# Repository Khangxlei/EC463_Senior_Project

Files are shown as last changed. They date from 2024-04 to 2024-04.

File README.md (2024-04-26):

# EC464 Senior Project: 40Hz Light Therapy

This README includes a brief overview and an introduction to how to get started on our project. 

## Project Overview

### Introduction

This project aims to develop an LED panel capable of emitting a consistent 40Hz flickering light. The 40Hz frequency is particularly chosen based on research suggesting its potential benefits in neurotherapeutic applications, especially for enhancing cognitive functions and possibly impacting disorders like Alzheimer's disease.

### Objectives

The primary objective of this project is to design and construct a reliable, efficient LED panel system that can maintain precise flicker frequencies, especially targeting the 40Hz range. Key goals include:

 - Precision: Achieve exact control over flicker frequency to ensure consistent 40Hz output.
 - Safety: Ensure the panel operates safely under all conditions, including extensive usage scenarios.
 - User-Friendliness: Develop a control interface that allows users to easily adjust and set the brightness as needed.

### Current State

The project has reached a significant milestone with the development of two final product models:

 - **T0 Model:** This is the base model featuring a large LED panel that can simply turn on and off, designed for stationary use where size and portability are not constraints.
 - **T9 Model:** A compact, innovative model that can attach to any modern smartphone case using Velcro. The T9 not only offers portability but also includes adjustable flickering brightness settings, making it ideal for personal use in a variety of settings.

## Installation

Installation comes in two parts: the software and the hardware. Here are the steps to help you get a quick-start on our project:

1. First you should install the software part of the project. Please refer to the Installation section under the [README_software.md](README_software.md) file
2. Next, you can set up the hardware of the project. Please refer to the section named "_Setting up the product_" under the [README_hardware.md](README_hardware.md) file. If you need help acquiring the materials needed, under the same file there is a Bill of Materials (BOM) section where you can find all the materials you will need for the project.
3. After completing all these steps, you should be all set for installment!

## System Overview

For this product we have 2 different models catered towards different purposes. The base model, which is the T0, is our very first version for our client’s needs, which serves to be a simple LED panel supported by a stand. We then have the T9 model that is more streamlined and compact compared to the T0 model, and serves for a more user-friendly experience.

### T0

The phone would be attached onto the panel using an integrated phone holder, and at the back of the panel is where the power button resides. Simply, press it and the user will be able to use their phone without having to hold it, while being exposed to 40Hz light that is proven to help with Alzheimer’s Disease and dementia. The figure down below shows that we have the power supply being the wall outlet connected to the power module that will help power up the circuit. The panel stand will hold the LED panel, in which we have an Arduino Nano as the microcontroller connecting the hardware and software components that will act as the controller to transfer an ON/OFF signal into the LED panel. 

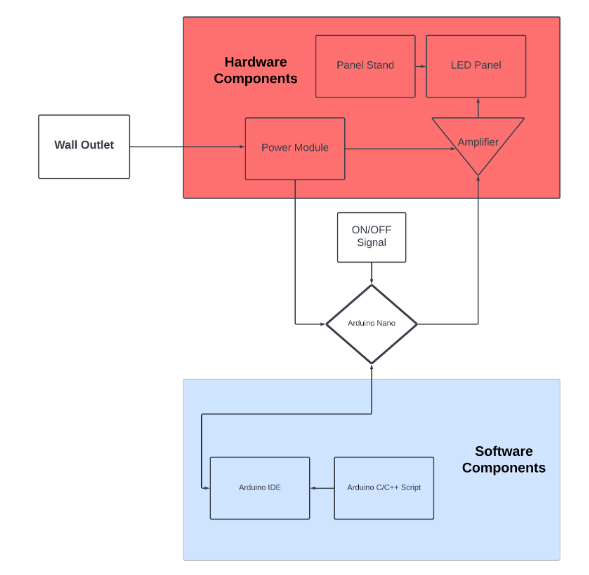
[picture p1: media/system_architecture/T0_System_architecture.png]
T0 System Architecture
 
  
[View PDF of T0 System Architecture](media/system_architecture/T0_System_architecture.pdf)

### T9

The figure down below is the overall system block diagram for the T9 model. It is a lot more streamlined and compact compared to the T9 model and is tailored more towards user’s convenience and needs. It has a phone cable that connects the phone into the microcontroller, which takes input of the brightness module and sends the corresponding signal to adjust the brightness of the LED accordingly. The software components for both models stay relatively the same as they are both compatible with Arduino code. 

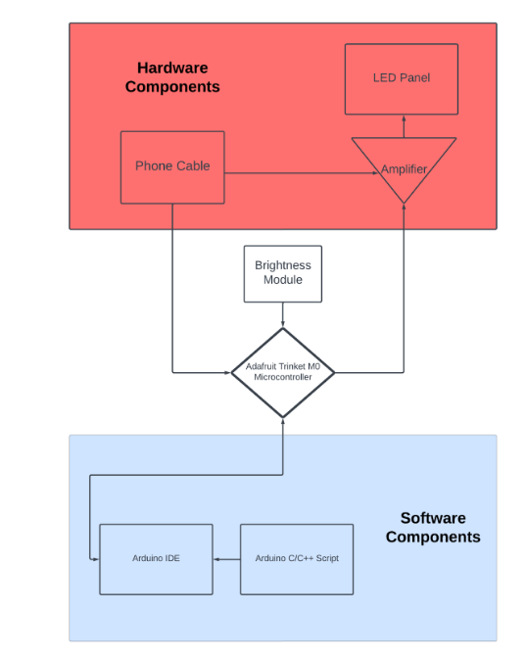
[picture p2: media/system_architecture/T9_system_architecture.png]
T9 System Architecture

  
[View PDF of T9 System Architecture](media/system_architecture/T9_system_architecture.pdf)

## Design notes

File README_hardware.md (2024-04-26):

# Hardware Schematics

## Circuit Diagram 

### T0
This is our circuit diagram for the T0 model. It uses pins 3, 4, and 5 as inputs and pins 5V and Ground as outputs. The circuit diagram illustrates an Arduino Nano wired with a button and a MOSFET towards an LED.
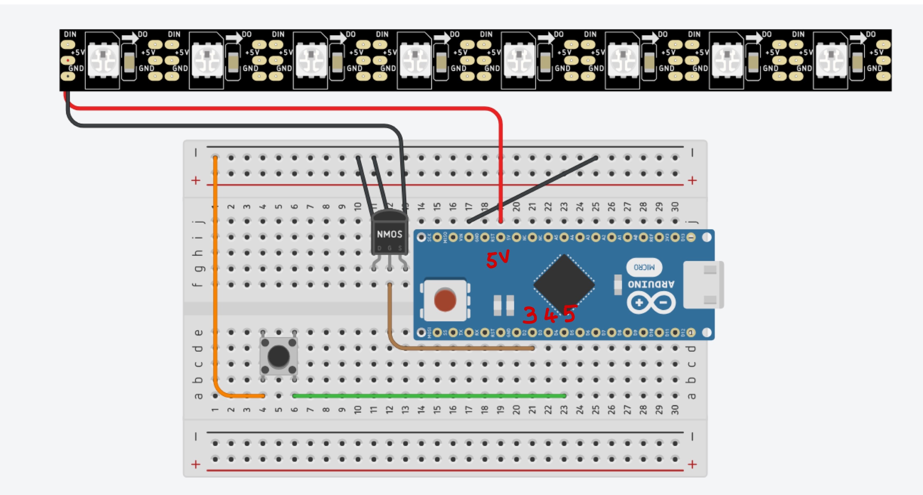
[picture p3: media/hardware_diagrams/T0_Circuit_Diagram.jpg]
Preview of T0 Circuit Diagram

[View PDF of T0 Circuit Diagram](media/hardware_diagrams/T0_Circuit_Diagram.pdf)

### T9
This is our circuit diagram for the T9 model. It uses pins 0, 3, and 4 as inputs and pins 3V and Ground as outputs. The circuit diagram illustrates an Arduino Nano wired with 2 buttons and a MOSFET towards an LED.

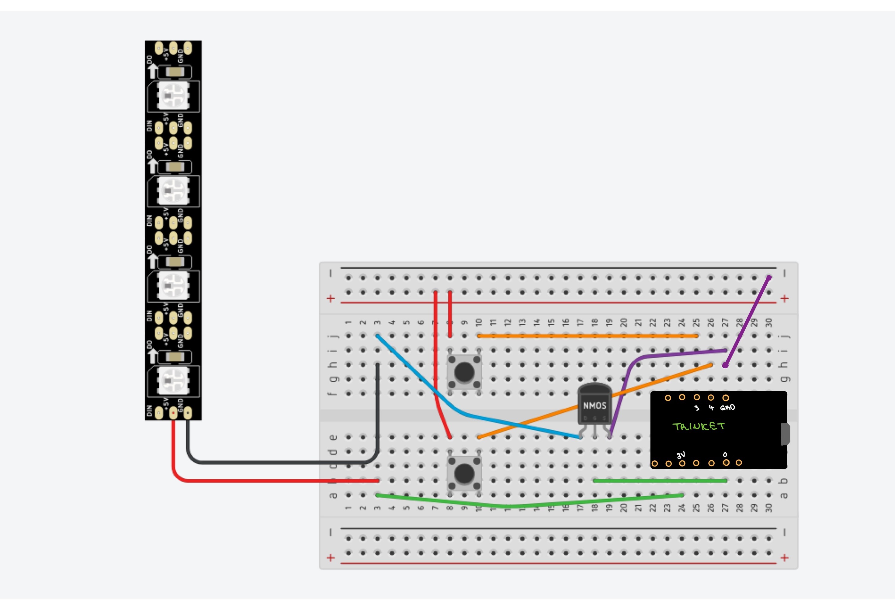
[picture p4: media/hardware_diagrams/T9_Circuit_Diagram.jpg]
Preview of T9 Circuit Diagram

[View PDF of T9 Circuit Digram](media/hardware_diagrams/T9_Circuit_Diagram.pdf)

## CAD Design

### T0 Housing

This is the CAD design for our T0 Housing. It consist of one button integrated along with an area for users to plug in the power cable to turn on the model. We have also uploaded the .stl file under the _hardware_diagrams/CAD_ folder and attached a PDF version of the CAD design down below.

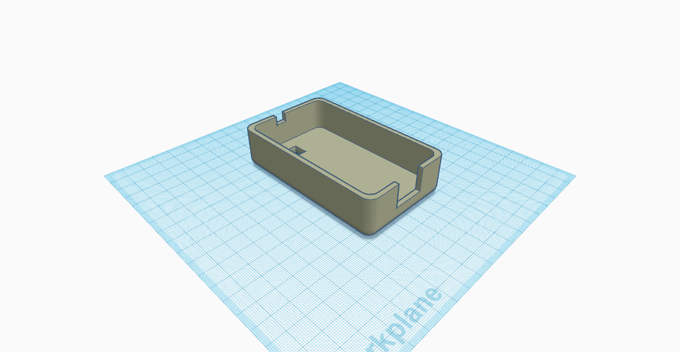
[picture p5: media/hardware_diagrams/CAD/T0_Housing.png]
T0 Housing
 [View PDF of T0 Housing](media/hardware_diagrams/CAD/T0_Housing.pdf)   

#### CAD File (.STL) 
Download the STL file for the T0 Model CAD design here: 
- [T0 STL CAD File)](media/hardware_diagrams/CAD/T0_Housing.stl)

### T0 Panel Stand
We used a pre-existing CAD design for a panel stand. This design allows 5 different angle configurations for the user to use the panel at whichever height they desire. We have also uploaded the .stl file under the _hardware_diagrams/CAD_ folder and attached a PDF version of the CAD design down below.

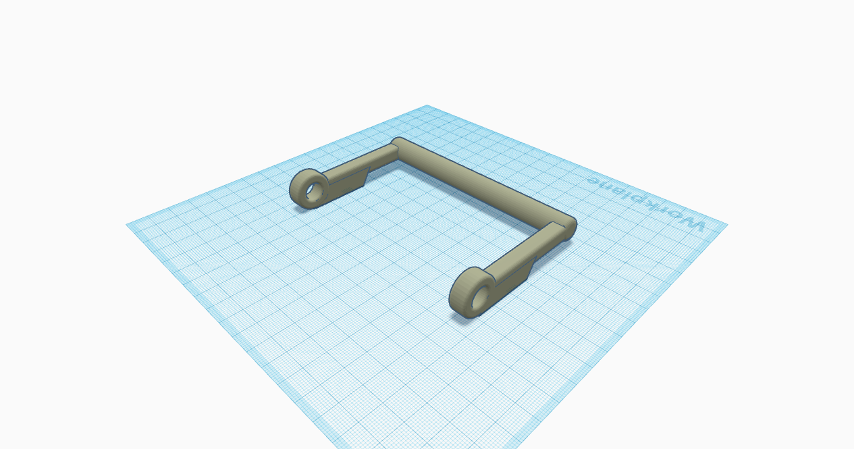
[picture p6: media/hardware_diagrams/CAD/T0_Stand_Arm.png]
T0 Stand Arm
 [View PDF of T0 Stand Arm](media/hardware_diagrams/CAD/T0_Stand_Arm.pdf)   
   
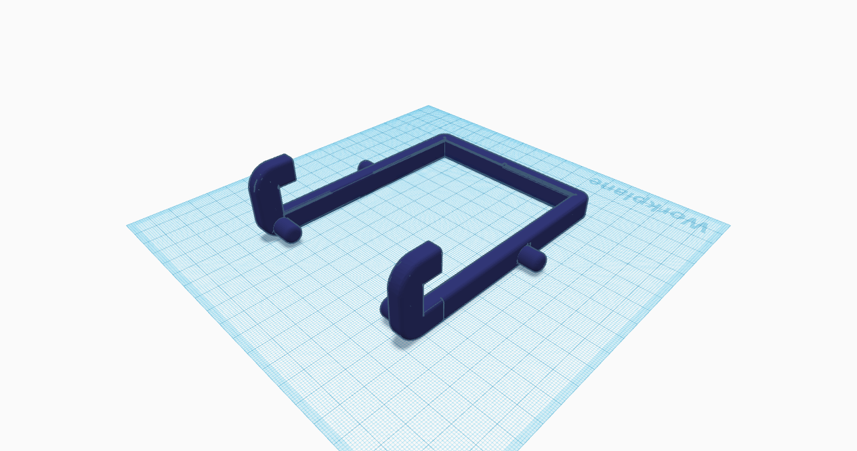
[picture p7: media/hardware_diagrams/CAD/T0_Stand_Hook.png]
T0 Stand Hook
 [View PDF of T0 Stand Hook](media/hardware_diagrams/CAD/T0_Stand_Hook.pdf)    
   
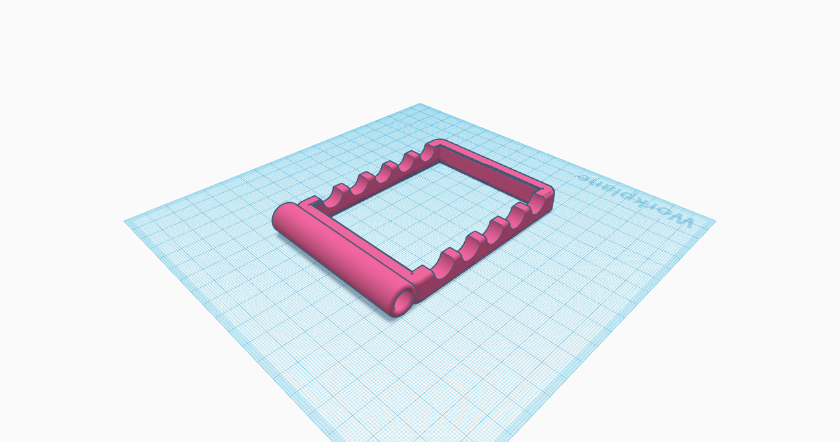
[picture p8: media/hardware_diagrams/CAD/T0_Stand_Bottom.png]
T0 Stand Bottom
 [View PDF of T0 Stand Bottom](media/hardware_diagrams/CAD/T0_Stand_Bottom.pdf)    

#### CAD File (.STL)
Download the STL file for the T0 Model CAD design here: _Emily should send the .stl files and replace that with this_
- [T0 Stand STL CAD File (1/3)](media/hardware_diagrams/CAD/T0_Stand_Arm.stl)
- [T0 Stand STL CAD File (2/3)](media/hardware_diagrams/CAD/T0_Stand_Bottom.stl)
- [T0 Stand STL CAD File (3/3)](media/hardware_diagrams/CAD/T0_Stand_Hook.stl)
  
### T9
This is the CAD design for our T9 Housing. It consist of 2 buttons integrated, along with a hollow bridge that allows the wires to run from the circuit board to the LED that is placed along the small panel above. It also has an open area to allow users to plug in their power cable. The .stl file is under the _hardware_diagrams/CAD_ folder and attached a PDF version of the CAD design down below.

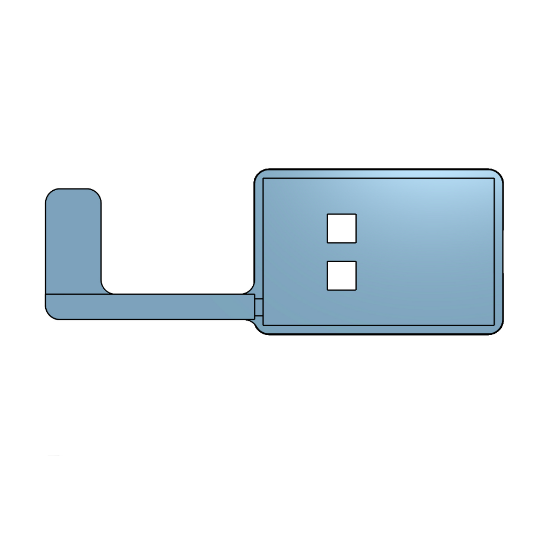
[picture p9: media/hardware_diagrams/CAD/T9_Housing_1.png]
T9 Housing (1/3)
 
   
[View PDF of T9 Housing 1](media/hardware_diagrams/CAD/T9_Housing_1.pdf)   
   
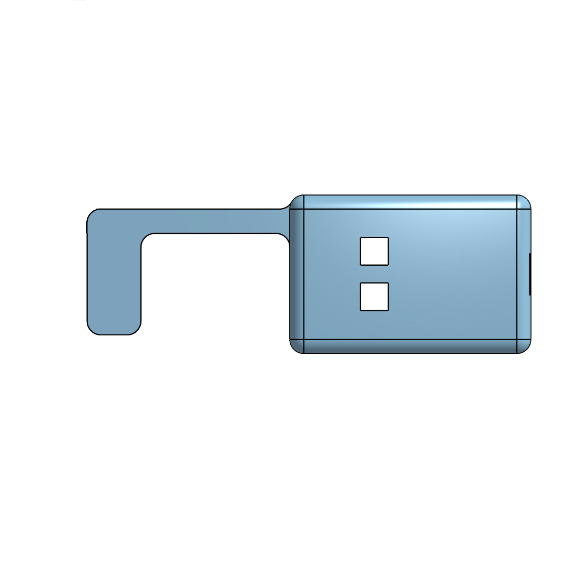
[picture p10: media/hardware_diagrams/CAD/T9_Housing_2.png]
T9 Housing (2/3)
 
   
[View PDF of T9 Housing 2](media/hardware_diagrams/CAD/T9_Housing_2.pdf)    
   
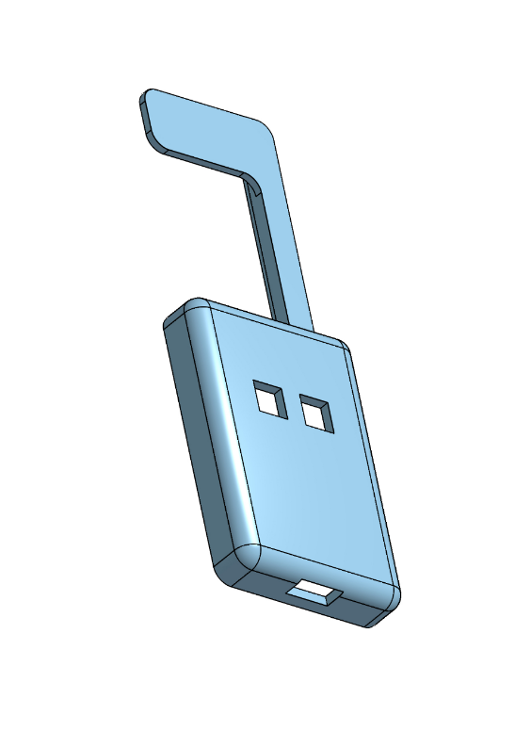
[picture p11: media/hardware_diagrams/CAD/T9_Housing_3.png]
T9 Housing (3/3)
 
   
[View PDF of T9 Housing 3](media/hardware_diagrams/CAD/T9_Housing_3.pdf)    

#### CAD File (.STL)
Download the STL file for the T9 Model CAD design here:
- [T9 STL CAD File (1/3)](media/hardware_diagrams/CAD/T9_Trinket_housing_cover.stl)
- [T9 STL CAD File (2/3)](media/hardware_diagrams/CAD/T9_Trinket_housing.stl)
- [T9 STL CAD File (3/3)](media/hardware_diagrams/CAD/T9_prototyping_board_housing.stl)

# Bill of Materials (BOM)
The following table includes a detailed list of all the materials used in the project, along with vendor information for each component:

| Item No. | Component                    | Quantity | Vendor Name        | Part Number | Price  |
|----------|------------------------------|----------|--------------------|-------------|--------|
| 1        | Adafruit Trinket M0 Trinket  | 1        | Adafruit           | 3500        | $8.95  |
| 2        | Arduino Nano + Cable         | 1        | Arduino            | A000005     | $24.90 | 
| 3        | Prototype Circuit Board      | 2        | Amazon             | B081MSKJJX  | $7.99  |
| 4        | LED Strip                    | 2        | Amazon             | B0C9919Z7Q  | $14.99 |
| 5        | LED Panel                    | 1        | Amazon             | B09VTCG1ZR  | $14.99 |
| 6        | Wires                        | 10-15    | Boston University  | N/A         | N/A    |
| 7        | Button                       | 3        | Boston University  | N/A         | N/A    |
| 8        | MOSFET                       | 2        | Boston University  | N/A         | N/A    |
| 9        | Velcro                       | 1        | Amazon             | 085-03-0026 | $9.29  |
| 8        | Micro-USB to USB-C Cable     | 1        | Amazon             | B094RDLNDB  | $9.99  |

## Vendor Information
Below is additional information about the vendors from whom components were purchased:

- **Adafruit Industries**
  - **Website:** [Adafruit.com](https://www.adafruit.com)
  - **Contact:** support@adafruit.com
  - **Phone:** (646) 248-7822

- **Arduino**
  - **Website:** [Arduino.cc](http://arduino.cc)
  - **Contact:** support@arduino.cc
  - **Phone:** N/A

- **Amazon**
  - **Website:** [Amazon.com](https://www.amazon.com/)
  - **Contact:** [Amazon Contact Page](https://www.amazon.com/gp/css/contact-us-access/ref=cu_surl_text_trace)
  - **Phone:** 1-888-280-4331

# Power Requirements

This section outlines the power specifications required to operate the 40Hz LED Panel effectively.

## T0 
### Voltage Requirements
- **Operating Voltage:** 5V
- **Minimum Voltage:** 0V
- **Maximum Voltage:** 5V

### Current Requirements
- **Operating Current:** 2 A
- **Peak Current:** 2.4 A (during operation)
- **Standby Current:** 10mA ~ 100mA (when idle)

### Power Consumption
- **Typical Power Consumption:** 10 Watts
- **Maximum Power Consumption:** 12 Watts (under full load)

## T9
### Voltage Requirements
- **Operating Voltage:** 3V
- **Minimum Voltage:** 0V
- **Maximum Voltage:** 3V

### Current Requirements
- **Operating Current:** 2 A
- **Peak Current:** 2.4 A (during operation)
- **Standby Current:** 10mA ~ 100mA (when idle)

### Power Consumption
- **Typical Power Consumption:** 6 Watts
- **Maximum Power Consumption:** 7.2 Watts (under full load)

### Additional Notes
- Make sure to use a power supply that matches or exceeds the required specifications.
- Avoid exposing the device to voltages above the maximum rating to prevent damage.
- For optimal performance, ensure stable current delivery especially during peak usage.

# System Pictures

This section provides a clear view of the system inside the enclosure. 

## T0 (inside enclosure)

These are pictures of the system circuit for the T0 model. This is what is inside the enclosure, before we placed a housing over it. The pictures displays the circuit board with the components that we used for the T0 model.

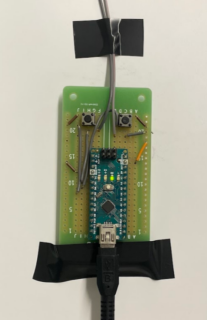
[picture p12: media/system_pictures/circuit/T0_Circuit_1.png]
System Circuit (1)

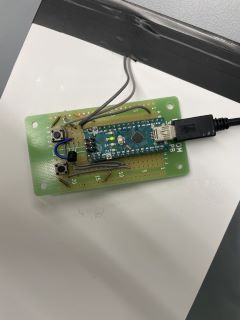
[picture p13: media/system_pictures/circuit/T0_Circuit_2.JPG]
System Circuit (2)


## T9 (inside enclosure)

The picture below shows the system for the T9 model. The two yellow wires are the power and ground wires connecting towards the LED. 

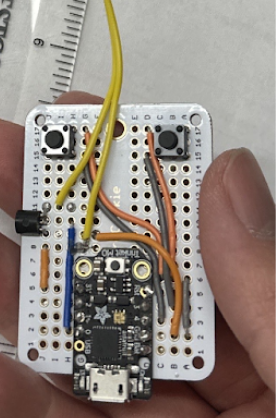
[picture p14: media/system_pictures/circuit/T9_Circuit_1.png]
System Circuit (1)


## T0 (with enclosure)

These are pictures of the system circuit for the T0 model. This is what is inside the enclosure, before we placed a housing over it. The pictures displays the circuit board with the components that we used for the T0 model.

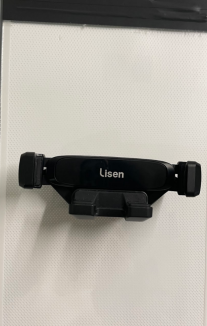
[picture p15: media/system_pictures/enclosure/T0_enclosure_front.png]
T0 Complete Circuit Front

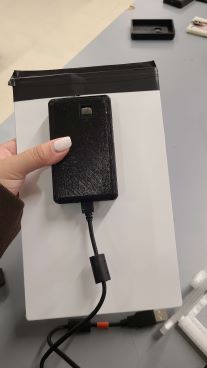
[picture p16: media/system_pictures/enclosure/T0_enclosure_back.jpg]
T0 Complete Circuit Back


## T9 (with enclosure)

The video below is a full demonstration of the T9 model. It is small and compact and there are buttons in the back that are used to adjust the brightness intensity of the LED. 

T9 Video with Enclosure

# Setting up the product

This section will document how to set up the hardware part of our project. For instructions on how to install the software system, please refer to the README_software.md. 

## T0

Place the phone onto the phone holder compartment at the front of the panel (illustrated below). 

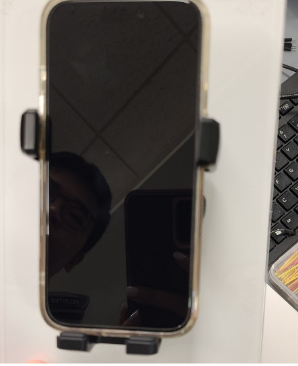
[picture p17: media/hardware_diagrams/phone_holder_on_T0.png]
Phone on Holder of T0


Now set up a circuit with the following schematic, same as the one that was shown in the circuit schematics section. Make sure to use the correct pins on the Arduino Nano!

Preview of T0 Circuit Diagram

From then, simply plug in the power cable for the Arduino Nano, click on the button and you should have a functioning 40 Hz flickering LED panel!

## T9

Setting up the T9 model is a lot simpler. Simply create the following circuit using the schematic below. From there, power the microcontroller using a micro-USB to USB-C cable and adjust the brightness using the two buttons. 

Preview of T9 Circuit Diagram

# Pictures of Final Product

## T0

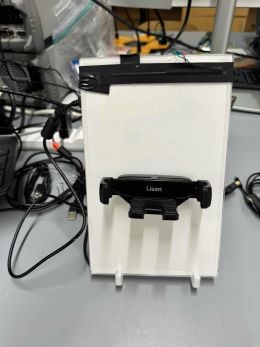
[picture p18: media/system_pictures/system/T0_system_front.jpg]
Picture of T0 System (Front)

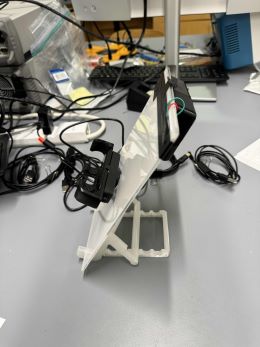
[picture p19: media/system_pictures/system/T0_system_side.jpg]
Picture of T0 System (Side)

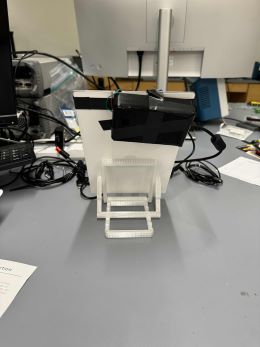
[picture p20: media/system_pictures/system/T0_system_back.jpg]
Picture of T0 System (Back)

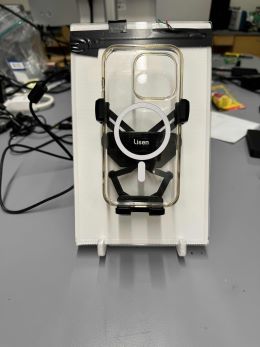
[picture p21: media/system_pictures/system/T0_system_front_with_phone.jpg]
Picture of T0 System (Front with Phone)


## T9

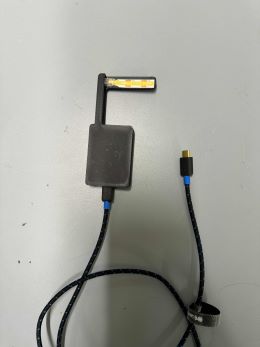
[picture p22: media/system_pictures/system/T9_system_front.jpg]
Picture of T9 System (Front)

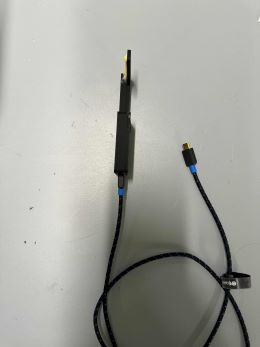
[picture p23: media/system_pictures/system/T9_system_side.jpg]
Picture of T9 System (Side)

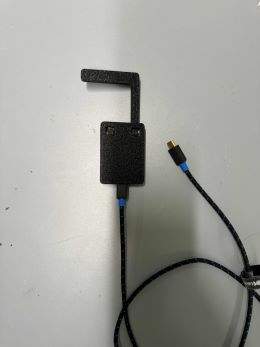
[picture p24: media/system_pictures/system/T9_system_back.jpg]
Picture of T9 System (Back)


# Notes
## Datasheets
 - [Datasheet for Trinket M0](https://cdn-learn.adafruit.com/downloads/pdf/adafruit-trinket-m0-circuitpython-arduino.pdf)
 - [Datasheet for Arduino Nano](https://docs.arduino.cc/resources/datasheets/A000005-datasheet.pdf)

## Web resources
 - [Arduino Nano Documentation](https://docs.arduino.cc/hardware/nano/)
 - [Operating LED Documentation](https://img.kwcdn.com/product-file-public/1fa3201b30/e1cf93ef936620d4e02b9221dc2b4623.pdf?_x_sessn_id=po0ericp0z&refer_page_name=goods&refer_page_id=10032_1714006419912_5y583ihzke&refer_page_sn=10032)
 - [Adafruit Trinket M0 Documentation](https://www.play-zone.ch/en/fileuploader/download/download/?d=1&file=custom%2Fupload%2FFile-1507818705.pdf)

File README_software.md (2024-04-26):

# Software

Since our project is mainly hardware, there is not much documentation needed for the software aspect of this project.

## Files

There are 2 files we have developed on Arduino IDE of file type: .ino, each of which are in charge of controlling our two microcontrollers: Arduino Nano and Adafruit Trinket M0. They .ino files are named respectively to their own microcontroller, Arduino_Nano.ino & Trinket_M0.ino. 

### Arduino_Nano.ino

This file is in charge of programming logic for our T0 model, which utilizes the Arduino Nano as its microcontroller. The Arduino program takes in a singular input pin, which is the button on pin 4, and it takes in an output pin which goes towards the LED at pin 3. Programming logic is that it toggles the brightness on and off every 12.5ms, which is half of 25ms because 25ms = 1/f = 1/40Hz. The code also incorporates a debouncer to recognize when the user clicks a button, it turns the brightness off immediately. The delay would not be interfering with the 40Hz, as it only has a delay at the start or end of the blinking cycle, so during its blinking there should not be interference.

### Trinket_M0.ino

This file is in charge of programming logic for our T9 model, which utilizes the Adafruit Trinket M0 as its microcontroller. The program this time takes in 2 input pins, being pin 3 and 4 for increase and decrease brightness buttons. It follows a similar logic as Arduino_Nano.ino, the only difference is that this time, it has a brightness variable that continuously changes every time one of the button pins gets pushed, in which it sends a signal to the program and we set the brightness variable accordingly to the button (0 being the minimum and 255 being the maximum). The analogWrite then displays the LED at whichever brightness the variable is on, and therefore we can adjust the brightness for our T9 model.

## Installation

### Arduino_Nano.ino

Installation for the Arduino Nano is simple, since the Nano is already a default board within Arduino IDE. Here are the steps:
 - First ensure you have the Arduino IDE software installed. You can download it here: [Install Arduino IDE](https://www.arduino.cc/en/software)
 - Download the _Arduino_Nano.ino_ file onto your desktop.
 - Open it via Arduino IDE.
 - At the top, click on the Dropdown where it says "_Select Board_", then click on "_Select other board and port_". A pop-up should then open.

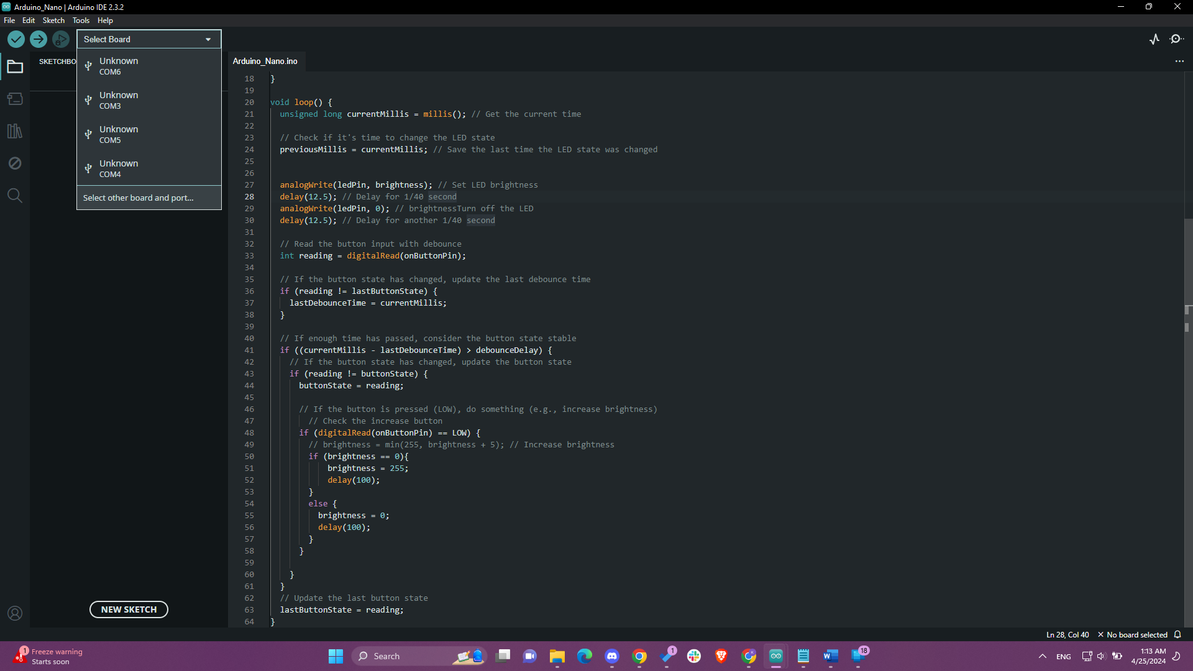
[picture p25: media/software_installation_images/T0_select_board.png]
Select board
   
   
 - On the pop-up, type in Nano and select "_Arduino Nano_", as well as the COM Port that you have the PC connected to with the Nano.

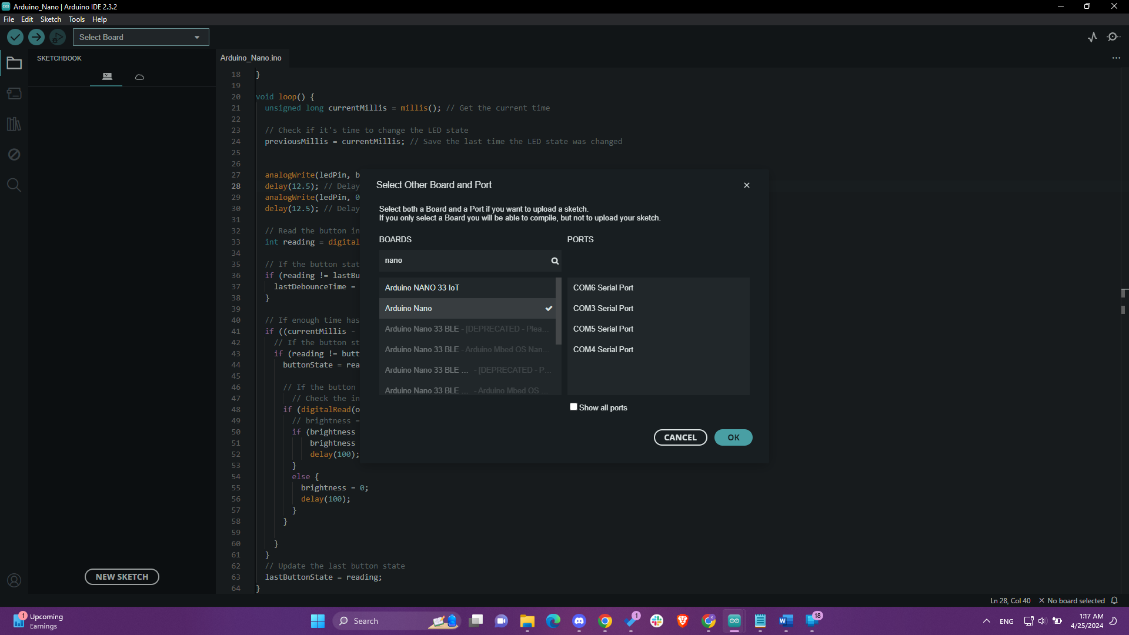
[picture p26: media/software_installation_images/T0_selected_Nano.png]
Selected board
   
   
 - Click OK.
 - Now simply click Upload (top left button with the arrow icon pointing to the right) and your code should now be embedded into the Arduino Nano!

### Trinket_M0.ino

 - First ensure you have the Arduino IDE software installed. You can download it here: [Install Arduino IDE](https://www.arduino.cc/en/software)
 - Download the _Trinket_M0_.ino_ file onto your desktop.
 - Open it via Arduino IDE.
 - At the top right, click Files > Preferences, or you can do it on your keyboard: Ctrl+Comma. At the bottom of the Preferences tab, there is a user input area for "_Additional boards manager URLs_". Paste in this link: <https://adafruit.github.io/arduino-board-index/package_adafruit_index.json>. If there are other links present, separate them with comma.

 Additional boards manager URLS

 - Next, open Boards Manager by clicking on Tools > Board > Boards Manager.
   
 Boards Manager

 - Search Arduino SAMD, and install the latest version of “Arduino SAMD Boards (32-bits ARM Cortex-M0+) by Arduino.

 SAMD Arduino

 - Next, search Adafruit SAMD, and install the latest version of Adafruit SAMD Boards by Adafruit. By now, you should be able to find the Trinket M0 in your list of boards. 

SAMD Adafruit

 - Close Boards Manager.
 
 - At the top, click on the Dropdown where it says "_Select Board_", then click on "_Select other board and port_". A pop-up should then open.

   Select board
   
 - On the pop-up, type in Trinket M0 and select "_Adafruit Trinket M0 (SAMD21)_", as well as the COM Port that you have the PC connected to with the Nano.

   Selected board
   
 - Click OK.
 - Now simply click Upload (top left button with the arrow icon pointing to the right) and your code should now be embedded into the Trinket!

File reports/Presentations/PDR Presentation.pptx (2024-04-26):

## Team 9 - Alzheimer’s Therapy

Bailey Brake, Ruohui Huang, Emily Lampat, Khang Le,
Yuri Zhang

## Introduction and Problem Statement

- Light Therapy
- AlzLife
- Light Attachment
Alzheimer’s and Dementia affect millions of americans each year. There is no cure, however, management of the cognitive decline seen in patients diagnosed with dementia plays a vital role in maintaining their quality of life.

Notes: Alzheimer’s and Dementia affect millions of americans each year. There is no cure, however, management of the cognitive decline seen in patients diagnosed with dementia plays a vital role in maintaining their quality of life. Though there is no known cure, researchers continue to look into maintaining cognition of patients and managing symptoms. AlzLife has developed an application that flashes the users screen while they play cognitive games.

## Requirements and Deliverables

- Flash at 40Hz
- Light intensity is visible to user
  - Adjustable light intensity
- Attach to smartphone
- Intuitive for user
- Subtle & ergonomic electronics housing
- Smartphone powered

## System Block Diagram


## Hardware


Circuitry
- Initial prototyping: Arduino Nano board
- Upcoming prototype: Adafruit Trinket board
- LED strip
- Brightness control buttons
Housing
- Current design: focus on compactness, then implement ergonomics



## Software

Arduino Software (IDE)
Arduino programming language (based on C/C++)
- Adjust LED brightness with two buttons.
- Pins: LED (3), Increase Button (4), Decrease Button (5).
- Blink Rate: 12.5ms intervals (40Hz).
- Code Mechanics: Uses PWM for brightness, analogWrite for LED control.
- Interaction: Press to increase/decrease brightness by 5, range 0-255.

## Testing procedure & results

1. Ensure Arduino is connected to a computer that has access to the code (https://github.com/rhhuang01/EC463Code/blob/main/Arduino) that generates PWM.
2. Compile and upload the script via the Arduino IDE.
3. Observe the oscilloscope and verify that the LED flickers within our desired time period.
4. Press the buttons to verify brightness is getting higher and lower corresponding to its own designated button, while maintaining the correct flicker frequency.


Circuit Setup

## Testing procedure & results (Cont.)


## Schedule


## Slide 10

Comments/Questions

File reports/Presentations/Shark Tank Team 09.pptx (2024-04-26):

## OptiSync Therapy

Synchronizing Light, Improving Your Life
An AlzLife Technology

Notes: BRAINSTORM:
AlzLife Light Frame

## Value Proposition


- For participants in Alzheimer’s clinical study, seeking to improve their cognition and sleep
- Our solution is a light frame to provide 40Hz therapy to attach to any phone
- Current 40Hz light therapy means require time set aside for the therapy: ours does not
Our product will meaningfully improve the therapy experience for patients of Alzheimer’s and dementia

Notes: Note that sometimes you need more than one value proposition. For example if the beneficiary does not pay you, then you need one value proposition for your beneficiary and one for your paying customer.

## Possible implementation: a visualization


## Minimum Viable Product


We need a light that flashes at 40 Hz at a consistent and comfortable intensity
It must attach to any phone case

## Technology Solution


Point 1: Advanced LED technology delivering consistent 40Hz frequency, maximizing therapeutic effects.
Point 2: Energy-efficient design ensuring extended use with minimal power consumption
Future step: Smart integration with an app allowing for tracking, reminders, and real-time feedback on therapy progress.

## Thank you!






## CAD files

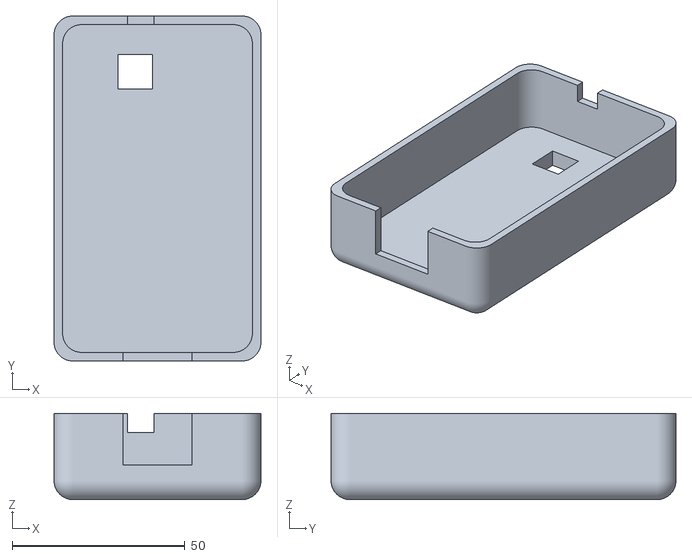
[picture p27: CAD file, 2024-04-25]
media/hardware_diagrams/CAD/T0_Housing.stl
60.0 x 100.0 x 25.0

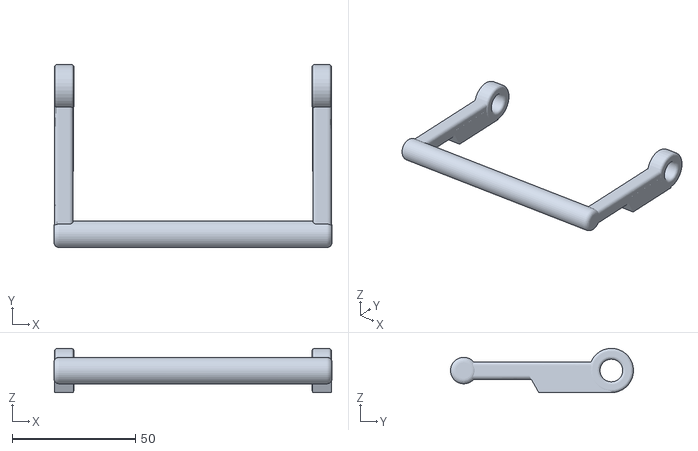
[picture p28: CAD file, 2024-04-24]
media/hardware_diagrams/CAD/T0_Stand_Arm.stl
113.0 x 74.4 x 18.0

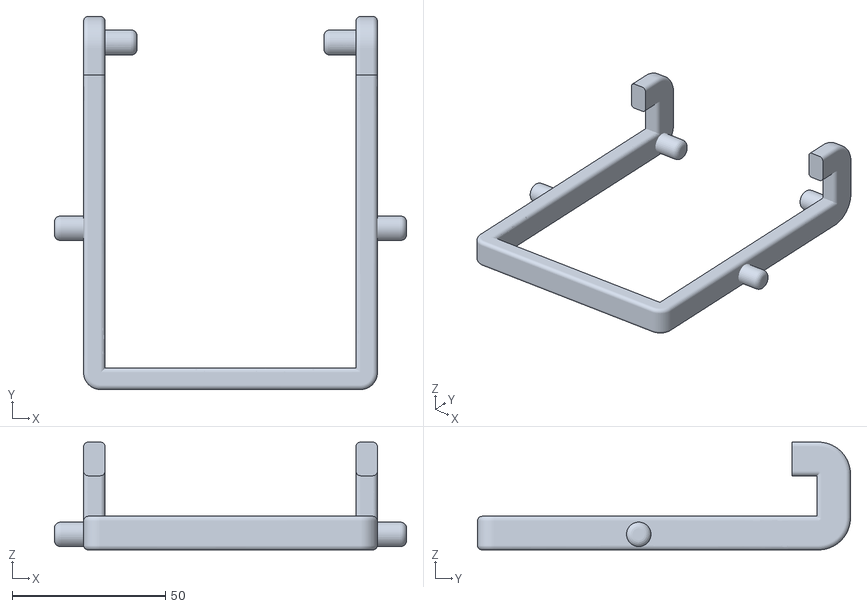
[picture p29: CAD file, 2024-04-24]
media/hardware_diagrams/CAD/T0_Stand_Hook.stl
115.2 x 121.9 x 35.2

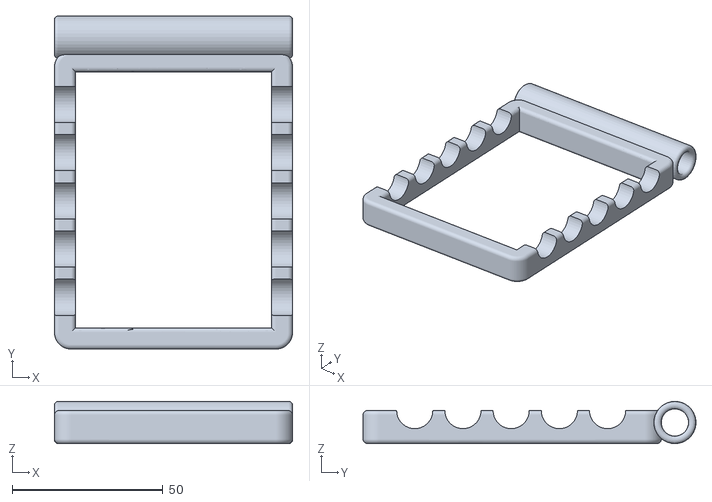
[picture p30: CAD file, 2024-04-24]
media/hardware_diagrams/CAD/T0_Stand_Bottom.stl
79.0 x 110.5 x 14.0

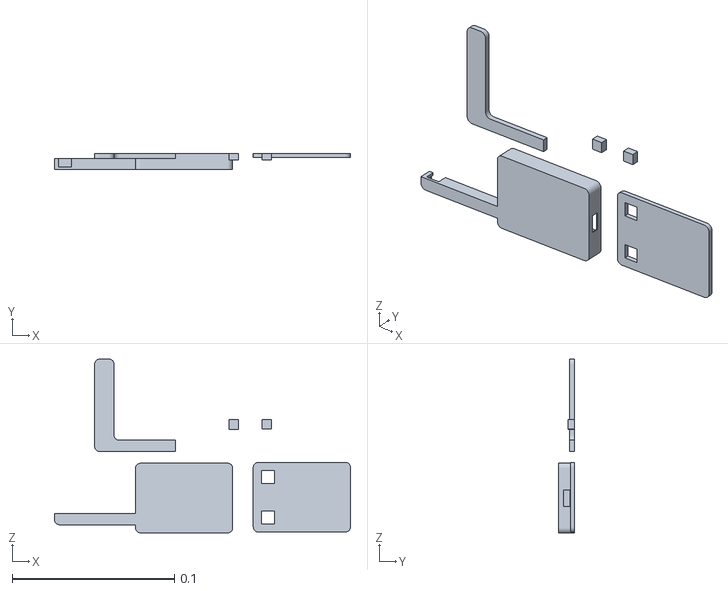
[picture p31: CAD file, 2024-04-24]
media/hardware_diagrams/CAD/T9_Housing_1.stl
0.183 x 0.01 x 0.107

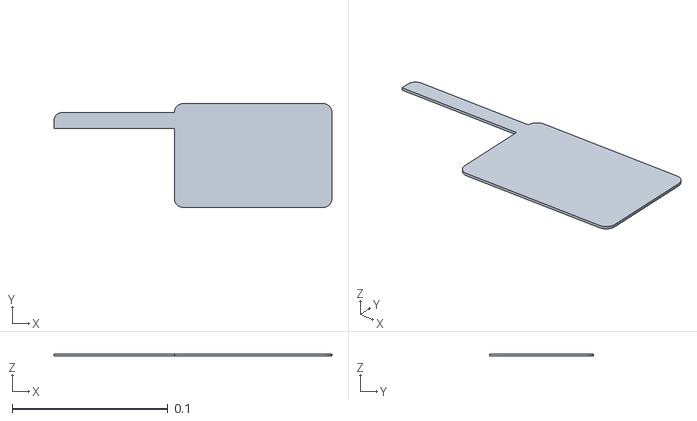
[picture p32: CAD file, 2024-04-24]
media/hardware_diagrams/CAD/T9_Housing_2.stl
0.178 x 0.0667 x 0.00146

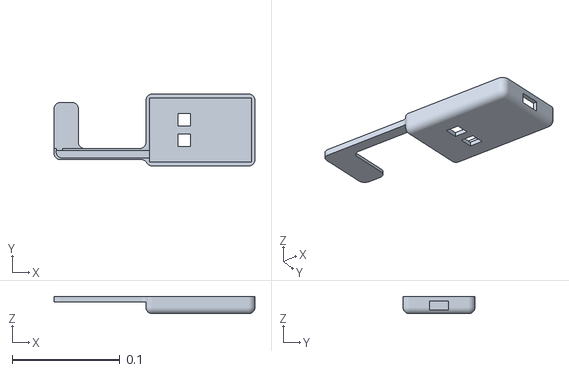
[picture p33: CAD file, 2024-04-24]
media/hardware_diagrams/CAD/T9_Housing_3.stl
0.186 x 0.0667 x 0.0161

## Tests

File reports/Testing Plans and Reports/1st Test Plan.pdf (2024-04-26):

# Boston University

# Electrical & Computer Engineering

## EC464 Senior Design Project

# Second Prototype Testing Plan

# OptiSync

by

Team 9

OptiSync

Team Members

Bailey Brake bbrake01@bu.edu

Ruohui Huang rhhuang@bu.edu

Emily Lampat lampat26@bu.edu

Khang Le khang@bu.edu

Yuri Zhang zyuri@bu.edu

1

### 1.0 Required Materials

Hardware:
- LED light
- Arduino Nano microcontroller
- Adafruit Trinket M0 microcontroller
- Circuitry Board
- Wires
- Buttons
Software:
- Arduino IDE
- Arduino script to generate 40Hz light frequency.
- Take buttons as input to write into LED output, acting as power source.

### 2.0 Set Up

Have the prototype where the circuitry board will be placed and stuck on the back of the LED panel. The wires will then connect from the Arduino Nano microcontroller into the LED that is placed at the front of our panel, We will also place a phone holder at the front that is glued onto it. Next, we will upload our code embedded into the Nano, plug it into a wall outlet and we are done with the setup.

### 3.0 Pre-Testing Setup Procedure

Pre-testing setup procedure is fairly simple. Please refer to the figures below to ensure that the setup is correct. All that is needed to do is connect the microcontroller into a wall plug and upload the

2

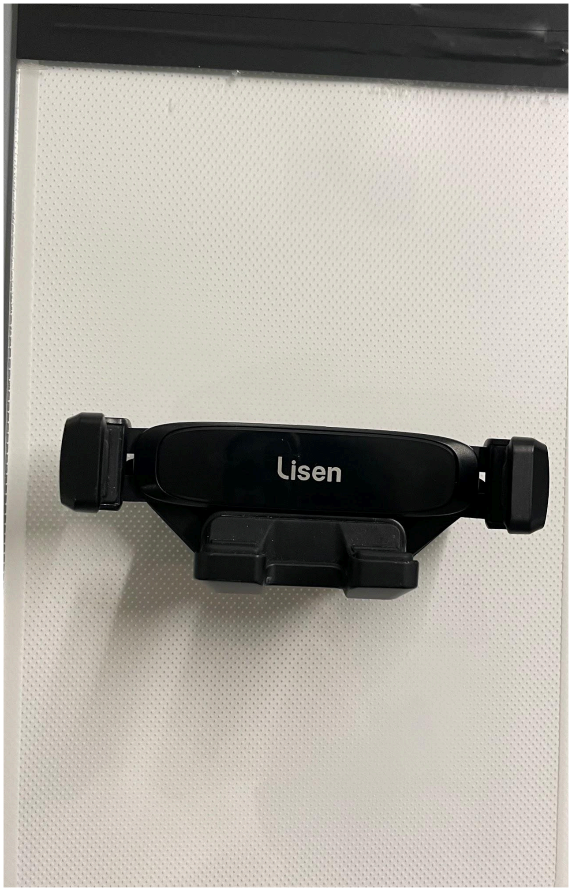
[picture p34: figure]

Figure 1. Front of LED Panel T0 Model

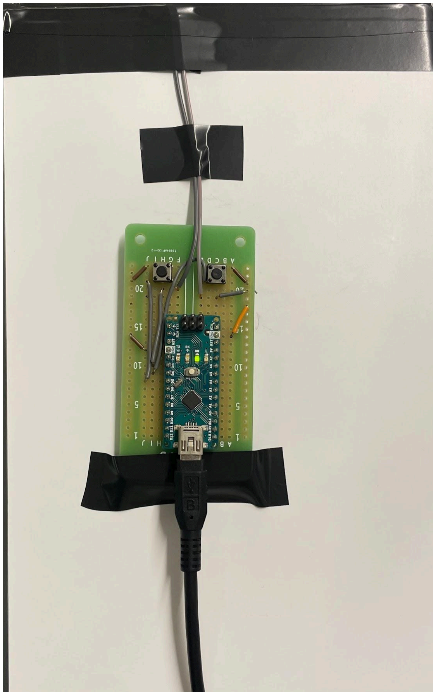
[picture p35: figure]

Figure 2. Back of LED Panel T0 Model

3

### 4.0 Testing Procedure

For the T0 model:
1. Ensure Arduino is connected to a wall outlet power source.
2. Verify that the LED status on the Arduino is lit up.
3. Press the button multiple times to verify the LED is receiving an ON/OFF signal.
4. Ensure that the phone holder is able to support the phone by placing the phone onto the holder attached to the panel.

### 5.0 Measurable Criteria

The criteria for having a successful running prototype are as follows
I. The circuit board should be intact with the LED panel.
II. | The LED should be at the front of the panel connected to the circuit board.
III. | Upon plugging in the microcontroller and pressing down the button, the LED should start
| flashing.
IV. | When toggling with the button, the LED should turn on and off within <1 second.

### 6.0 Hardware Pinout

T0 model:

Pin Number | Usage/Description
3 | White LED Output
4 | LED ON/OFF Button Input

4

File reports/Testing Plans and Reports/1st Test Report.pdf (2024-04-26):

# Memo

To: Professor Pisano
From: Yuri Zhang, Bailey Brake, Ruohui Huang, Emily Lampat, Khang Le Team: 9
Date: 11/19/2023
Subject: 1st Prototype Test Report

## 1.0 Test Setup

### 1.1 Bill of Materials:

| Hardware: ● LED Light: Selected for its efficiency and brightness, which are crucial for our application. ● Arduino Trinket Microcontroller: Chosen for its compact size and lack of unnecessary functions, making it ideal for our streamlined prototype. ● Oscilloscope: Essential for accurately measuring the LED's flicker frequency and ensuring our product meets the required specifications. ● Probes/Wires: For connecting and testing the circuit. ● Resistors: Calculated to match the LED's specifications, ensuring optimal current flow without risking damage. ● Laptop Computer: Used for programming the Arduino and monitoring the test. ● Tactile Push Buttons: For manual control over the LED's brightness levels. Software: ● Arduino IDE ○ Arduino script to generate 40Hz light frequency. ○ Take buttons as input to write into LED output, adjusting its brightness.

### 1.2 Setup Procedure:

| Our setup has been carefully designed to replicate a natural application environment.
| The Arduino Trinket is the central control unit connected to the laptop via a USB connection. This setup is essential for programming the microcontroller and allows real-time monitoring and adjustments during testing. An oscilloscope is used to continuously monitor the electrical characteristics of the LEDs, including flicker frequency and brightness levels. Two probes

1

from an oscilloscope were connected to the LED to measure the output frequency, given the difficulty of observing the 40Hz flicker rate with the naked eye.
The setup process involves careful calibration of the device. The LEDs are connected to the Arduino Trinket through a series of resistors and wires, ensuring that the current flowing through the LEDs is within safe limits. Tactile buttons are integrated into the circuitry to adjust the brightness of the LEDs manually. This setup aspect is essential because it simulates the end user's interaction with the product.

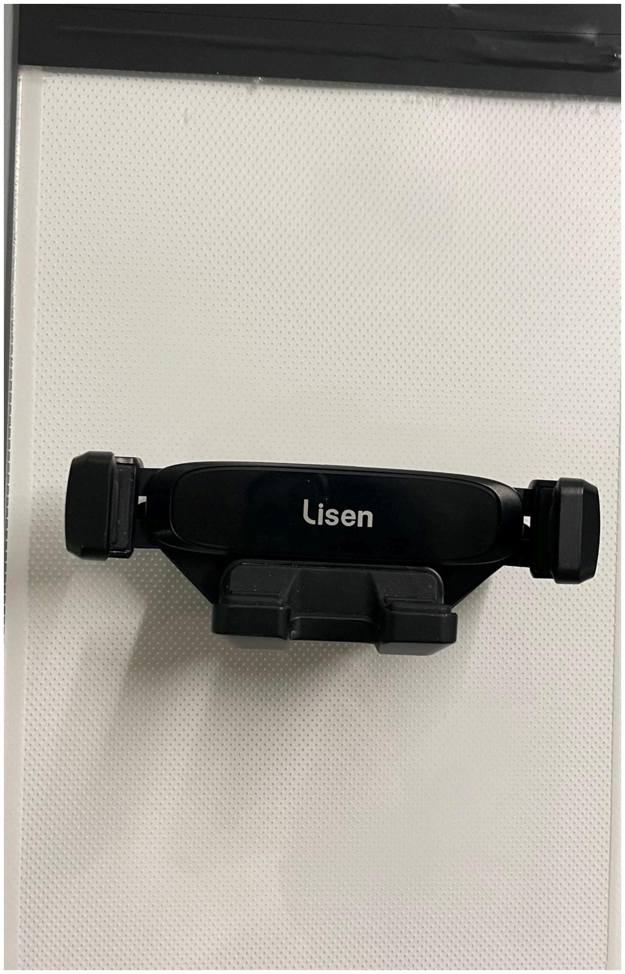
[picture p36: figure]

### Figure 1. Front of LED Panel T0 Model

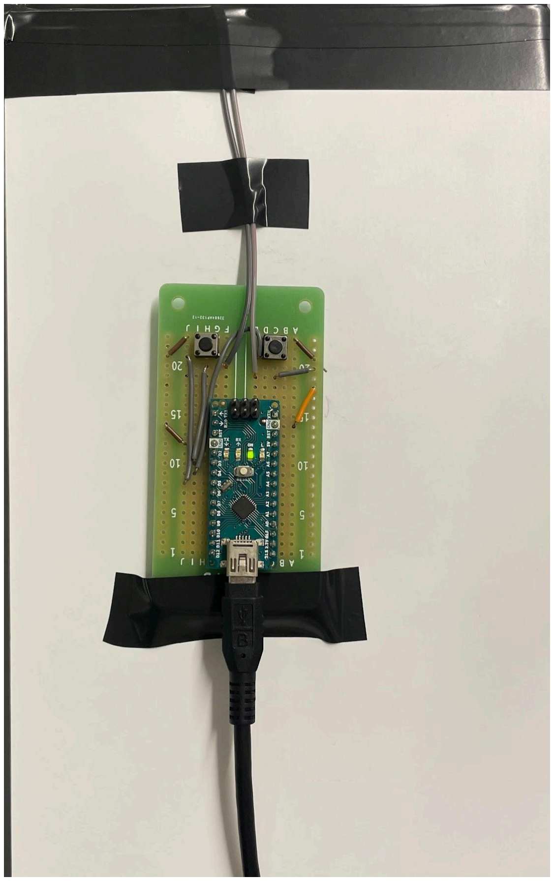
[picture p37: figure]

### Figure 2. Back of LED Panel T0 Model

2

### Figure 1: Illustration of Circuit Setup

## 2.0 Results and Measurements

### 2.1 Flicker Frequency Measurement:

In order to measure the flicker frequency, we set a time interval of 25ms on the oscilloscope, which is the desired time period of a flicker, considering we want 40Hz and t = 1/f = 1/40Hz = 0.025s. The LED's on-off cycle was observed to be consistent within this timeframe, with a deviation of less than 0.5ms, indicating high precision in frequency control.

### 2.2 Brightness Adjustment Measurement:

As for the brightness adjustments, we had two buttons separately increasing/decreasing the brightness. During our testing, as we pressed and held each button, the brightness gradually increased/accordingly reduced to the controller. Once it reached a maximum of brightness/dimness, it stayed there. We could turn it back on by pressing and holding the button. The brightness control was tested over a range of 0 to 255 in 10 increments. Each button press resulted in a smooth transition between brightness levels, with the oscilloscope showing a corresponding change in voltage across the LED. The maximum and minimum brightness levels were consistent across multiple tests, demonstrating the reliability of our control mechanism.

## 3.0 Conclusion and In-Depth Analysis

### 3.1 Conclusion:

The prototype test successfully demonstrated the core functionalities of our design. The Arduino script effectively maintained a 40Hz flicker frequency, which is crucial for our application's requirements. The manual brightness adjustments were responsive and precise, indicating a well-designed user interface.

### 3.2 Future Directions:

Our next steps involve transitioning to the Trinket M0 microcontroller for a more compact and efficient design. We will also integrate LED strips per our client's request and proceed with soldering to ensure robust and reliable connections. Further, we plan to conduct extensive user testing to refine the interface and ergonomics of our product.

### 3.3 Reflective Analysis:

The test setup and results aligned with our initial test plan, validating our equipment choices and design approach. The precision in flicker frequency control and the effective brightness adjustment mechanism were crucial achievements. In subsequent iterations, we will continue refining our design, enhancing circuit efficiency and user experience.

3

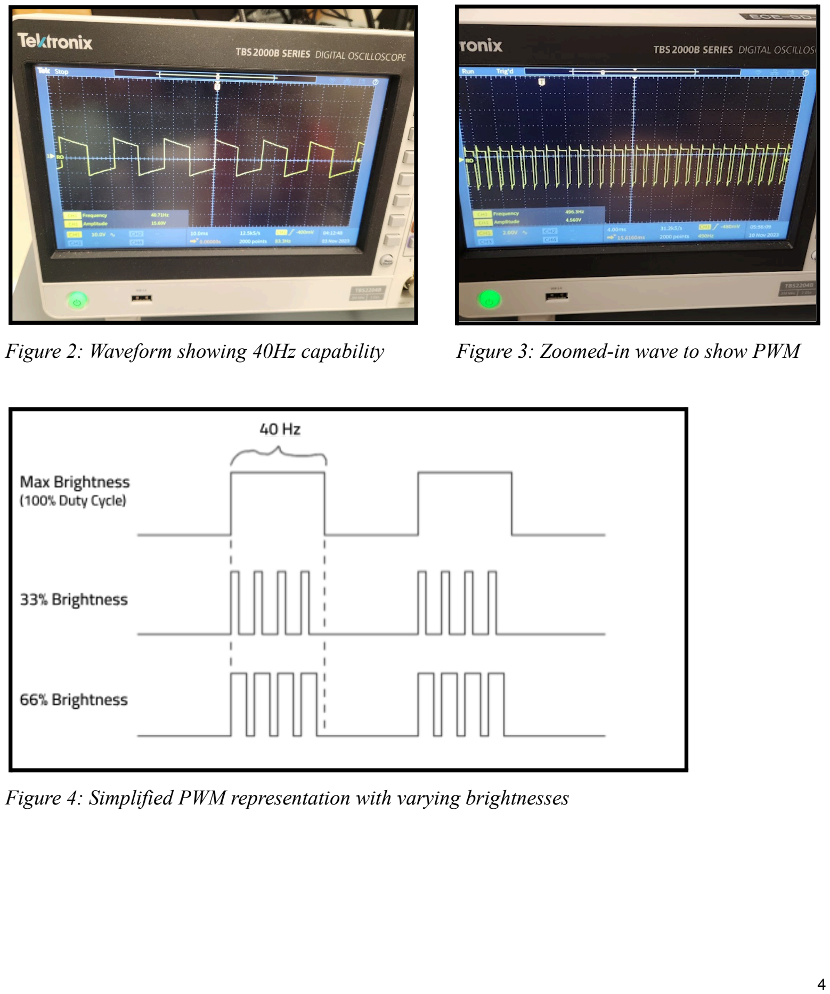
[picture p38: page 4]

Figure 2: Waveform showing 40Hz capability | Figure 3: Zoomed-in wave to show PWM

### Figure 4: Simplified PWM representation with varying brightnesses

4

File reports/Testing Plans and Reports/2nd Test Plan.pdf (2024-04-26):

# Boston University

# Electrical & Computer Engineering

## EC463 Senior Design Project

# First Prototype Testing Plan

# OptiSync

by

Team 9

OptiSync

Team Members

Bailey Brake bbrake01@bu.edu

Ruohui Huang rhhuang@bu.edu

Emily Lampat lampat26@bu.edu

Khang Le khang@bu.edu

Yuri Zhang zyuri@bu.edu

### 1.0 Required Materials

Hardware:
- LED light
- Arduino microcontroller + cable connector
- Oscilloscope
- Probes/Wires
- Resistor (depending on which light)
- Laptop computer
- Buttons
Software:
- Arduino IDE
- Arduino script to generate 40Hz light frequency.
- Take buttons as input to write into LED output, adjusting its brightness.

### 2.0 Set Up

The laptop computer serves as a power source for the moment since, in the end, we will want to be using a smartphone as the power source. The laptop also serves as the code generator for the Arduino and currently our brightness and frequency for the LED are determined by the code. The Arduino Nano serves as the power source for the LED and gives an output voltage of 5V. The oscilloscope allows us to measure the output frequency since 40Hz is very difficult to observe with the naked eye. The light that we are planning on using for this project is a white LED.

### 3.0 Pre-Testing Setup Procedure

Have a laptop connected to Arduino Nano using a USB cable. Attach the positive and negative probes on either side of the LED (in parallel), and then plug in the BNC end of the cable to the oscilloscope. Finally, have two buttons connected to any digital pins of the Arduino.

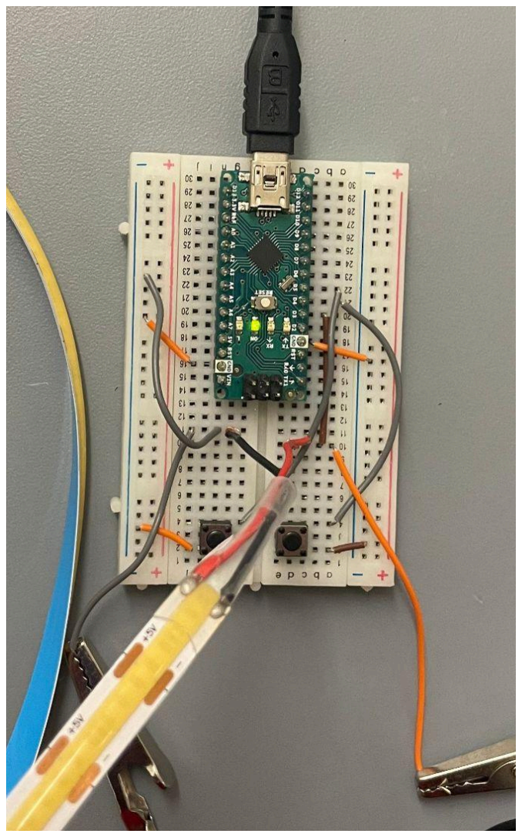
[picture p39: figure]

Figure 1: Illustration of Circuit Setup

### 4.0 Testing Procedure

1. Ensure Arduino is connected to a computer that has access to the code that generates PWM.
2. Compile and upload the script via the Arduino IDE.
3. Observe the oscilloscope and verify that the LED flickers within our desired time period.
4. Press the buttons to verify brightness is getting higher and lower corresponding to its own designated button, while maintaining the correct flicker frequency.

### 5.0 Measurable Criteria

The criteria for having a successful running prototype are as follows:
I. The LED strip should be able to connect to the breadboard and Arduino.
II. | Our output LED should flash at a rate of 40 flashes per second, or 40Hz.
III. | One button should increase the brightness of the LED, whilst maintaining the 40Hz flicker
| frequency.
IV. | Another button should decrease the brightness of the LED, also maintaining the 40Hz
| flicker frequency.

V. When the LED is turned off, the increase brightness button should turn it back on.

### 6.0 Hardware Pinout

Pin Number | Usage/Description
3 | White LED Output
4 | Increase Brightness Button Input
5 | Decrease Brightness Button Input

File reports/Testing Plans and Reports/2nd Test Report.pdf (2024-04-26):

# Memo

To: Professor Pisano
From: Bailey Brake, Ruohui Huang, Emily Lampat, Khang Le, Yuri Zhang Team: 9
Date: 3/8/2024
Subject: 2nd Prototype Test Report

## 1.0 Test Setup

### 1.1 Bill of Materials:

Hardware:
- LED Light: Selected for its efficiency and brightness, which are crucial for our application.
- Arduino Nano Microcontroller: Chosen for its compact size and lack of unnecessary
| functions, making it ideal for our streamlined prototype.
- Oscilloscope: Essential for accurately measuring the LED's flicker frequency and ensuring
| our product meets the required specifications.
- Probes/Wires: For connecting and testing the circuit.
- Laptop Computer: Used for programming the Arduino and monitoring the test.
- Tactile Push Buttons: For manual control over the LED's ON/OFF Level. Software:
- Arduino IDE
| ○ Arduino script to generate 40Hz(±1Hz) light frequency.

### - Take buttons as input to write into LED output, acting as power source

### 1.2 Setup Procedure:

Our setup has been carefully designed to replicate a natural application environment. We have a pre-test setup and a setup procedure. In order to ensure our test goes seamlessly, we have uploaded the Arduino code onto our Arduino Nano, and have the Nano along with the circuitry board be integrated onto the back of our LED panel. At the front, we have placed the phone holder where the user places their phone and is able to use it.
As for the setup before our prototype test, we simply connect the Arduino Nano into a wall plug as the power source, place a temporary stand so that our LED panel does not have to put it

1

flat onto the table. All of the setup procedures went accordingly to plan, as outlined in our test plan. Below are pictures of how our prototype test setup turned out to be.


### Figure 1. Front of LED Panel T0 Model


### Figure 2. Back of LED Panel T0 Model

2

## 2.0 Results and Measurements

### 2.1 Flicker Frequency Measurement:

In order to measure the flicker frequency, we set a time interval of 25ms on the oscilloscope, which is the desired time period of a flicker, considering we want 40Hz and:

t =

1
f =

1
40Hz = 0. 025s

The LED's on-off cycle was observed to be consistent within this timeframe, with a deviation of less than 0.5ms, indicating high precision in frequency control. Below was the result for our flickering rate, where the span that we see at the top was set to be 0.5ms, which encapsulated the cycles of on/off.

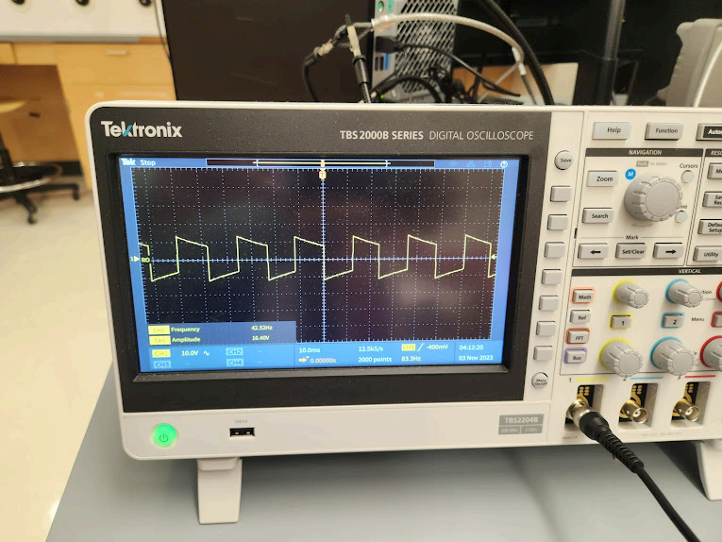
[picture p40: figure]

### Figure 3. Oscilloscope Reading from T0 model

### 2.2 ON/OFF Toggle Button Measurement:

For our ON/OFF toggle signal button, we measured how long it takes for the LED flickering to turn off upon a click on the button. We made several measurements with different intervals of the button click, to ensure that our debouncer was working properly and that the signal was being transmitted flawlessly with no delay or latency. The intervals between each toggle consisted of:
{2 seconds, 1 second and 50 millisecond} apart. The result was that the LED was able to turn on and off according to the button click well within 1 second.

3

## 3.0 Conclusion and In-Depth Analysis

### 3.1 Conclusion:

In conclusion, our decision to only test the T0 model with Professor Hirsch led to success. We were able to prove that our model was functioning at the proper level through observation as well as measurement with an oscilloscope. Our model was bright enough that the user could see the light flickering, even in a well-lit room, and the flickering was visible to the naked eye. Since this was the base model, it only had on/off functions which worked smoothly.

### 3.2 Future Directions:

Our next steps for our project are to continue work on the T9 model. We have the circuit functioning, however, transitioning it to a circuit board from a breadboard has been somewhat difficult since the connections can become unstable. We will also continue with our housing models for both the T0 and the T9 models. Overall, the circuits are presentable, but there is still progress needed on creating two visually appealing and easily understood products.

### 3.3 Reflective Analysis:

The T0 and T9 utilize very similar circuitry, but their forms are different. A successful test of the T0 is a good sign for the T9. Testing the T0 resulted in a clear view of how its form should be improved: for example, the LED panel should be propped up by arms on the housing to provide a simpler user experience. This same testing procedure on the T9 will similarly clarify its form. These sort of conclusions are difficult to quantify, but warrant mentioning, as user experience is crucial to these designs.

4

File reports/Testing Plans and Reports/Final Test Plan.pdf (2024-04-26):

# Boston University

# Electrical & Computer Engineering

## EC464 Senior Design Project

# Final Prototype Testing Plan

# OptiSync

by

Team 9

OptiSync

Team Members

Bailey Brake bbrake01@bu.edu

Ruohui Huang rhhuang@bu.edu

Emily Lampat lampat26@bu.edu

Khang Le khang@bu.edu

Yuri Zhang zyuri@bu.edu

1

### 1.0 Required Materials

Hardware:
- T0 model
- T9 model
- Oscilloscope
- Cables
- BNC to hook
- USB-A to mini USB
- USB-C to micro-USB
Software:
- Arduino IDE
- Arduino script to generate 40Hz light frequency.
- Take buttons as input to write into LED output, acting as power source. ■ T0 model: ON/OFF
■ T9 model: brightness adjustability

### 2.0 Set Up

### 2.1 T0 model set up

Our T0 model consists of an arduino nano microcontroller that receives the button on/off input and outputs a flickering rate of 40Hz for our LED. There is a MOSFET that will boost the current supplied to the LED without surpassing the microcontroller output capabilities.

### 2.2 T9 model set up

Our T9 model consists of an adafruit trinket microcontroller that receives increase/decrease input from two buttons, and outputs a flickering rate of 40Hz for our LED. There is also a MOSFET in this circuit that boosts the current supplied to the LED.

2

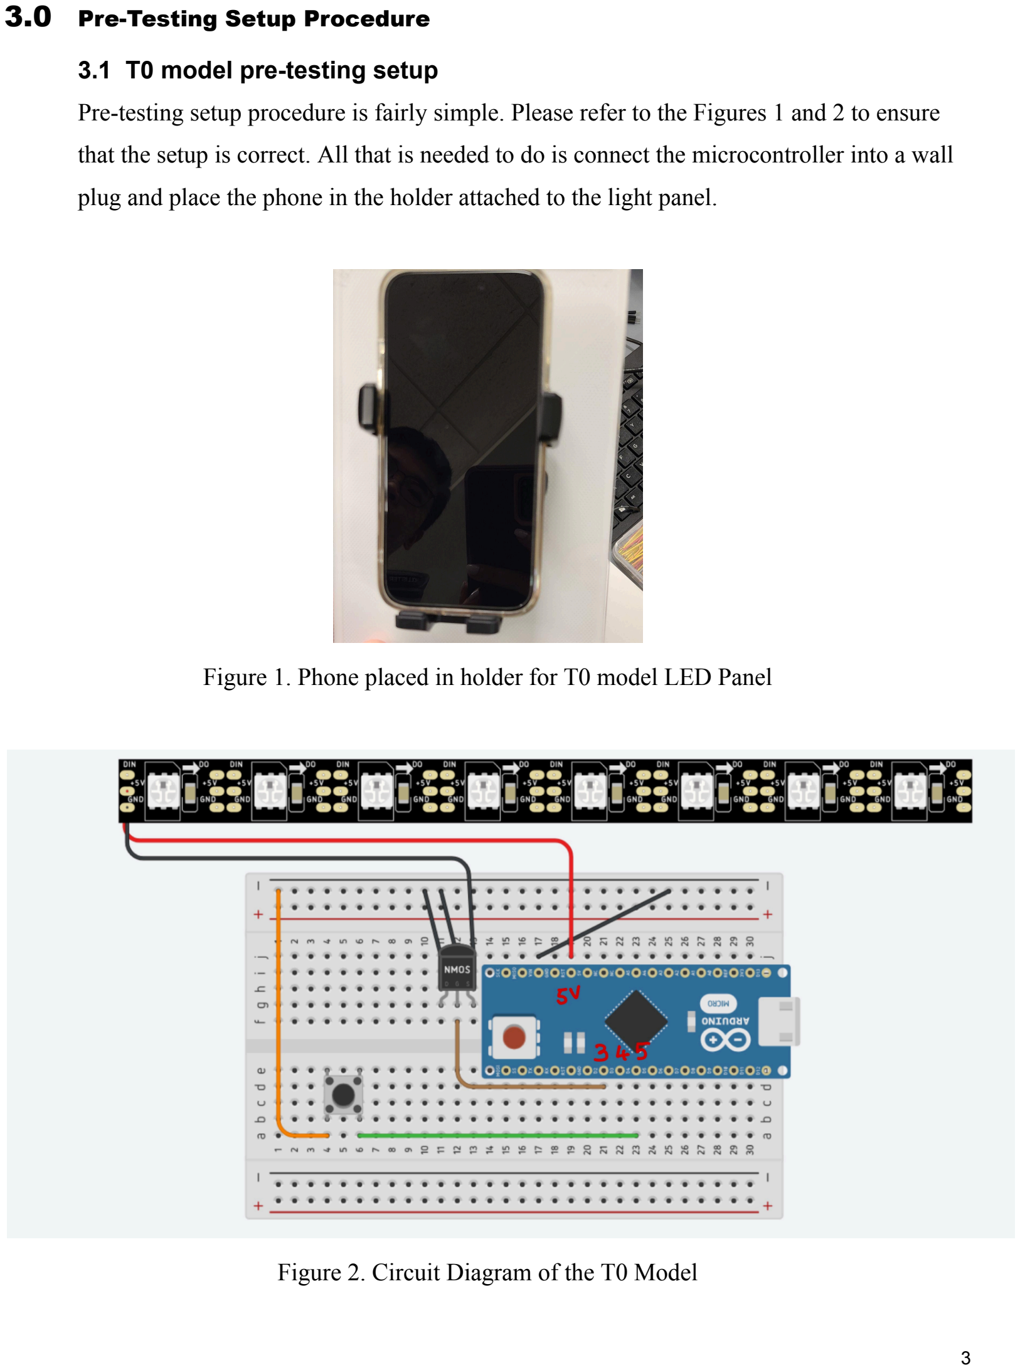
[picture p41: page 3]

### 3.0 Pre-Testing Setup Procedure

### 3.1 T0 model pre-testing setup

Pre-testing setup procedure is fairly simple. Please refer to the Figures 1 and 2 to ensure that the setup is correct. All that is needed to do is connect the microcontroller into a wall plug and place the phone in the holder attached to the light panel.

Figure 1. Phone placed in holder for T0 model LED Panel

Figure 2. Circuit Diagram of the T0 Model

3

### 3.2 T9 model pre-testing setup

This is the hand-held option that we have made, so setup is a little bit different from the T0 model. Please refer to Figure 3 to ensure that the setup is correct. Attach the T9 model to the back of the phone using velcro and plug the microcontroller into the power port of the phone. The cable would have to be micro-usb to usb-c connection.

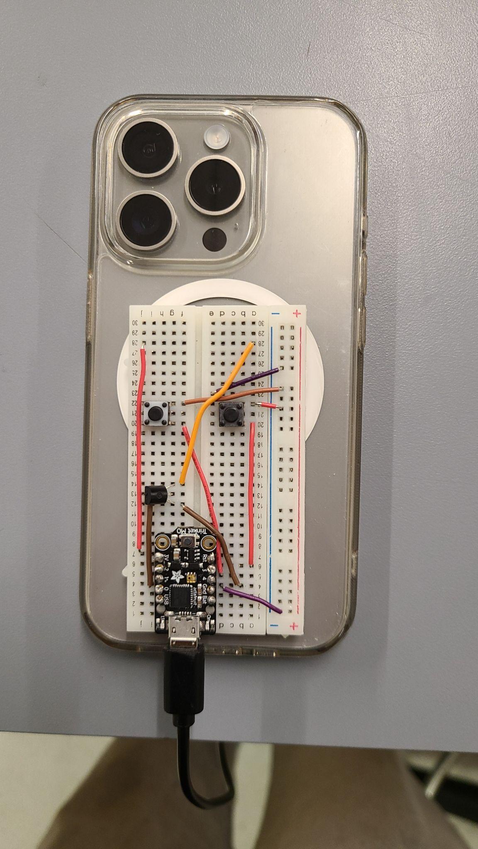
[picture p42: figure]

Figure 3. T9 model attached to the back of the phone.

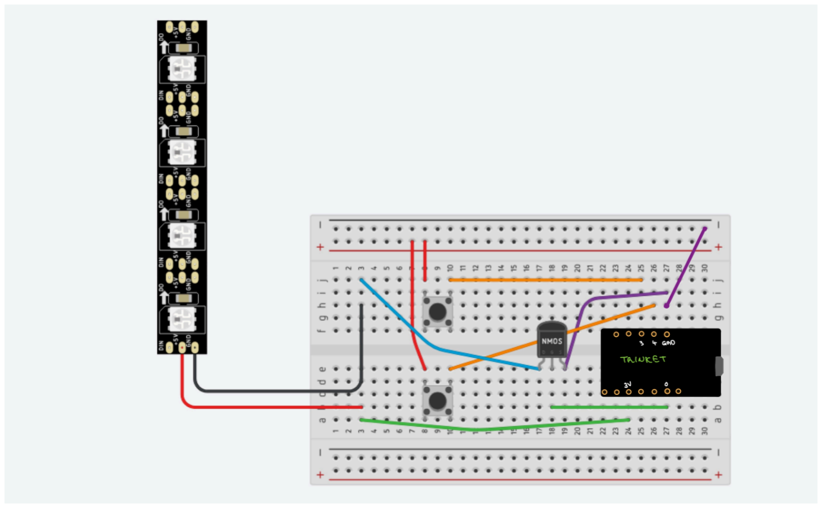
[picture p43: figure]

Figure 4. Circuit Diagram of the T9 model

4

### 4.0 Testing Procedure

### 4.1 T0 model:

1. Ensure Arduino is connected to a wall outlet power source.
2. Verify that the LED status on the Arduino is lit up.
3. Press the button multiple times to verify the LED is receiving an ON/OFF signal.
4. Ensure that the phone holder is able to support the phone by placing the phone onto the holder attached to the panel.
5. Use probe wires to verify frequency with oscilloscope

### 4.2 T9 model:

1. Attach T9 model to the back of a smartphone
2. Ensure Arduino is connected to the phone power port.
3. Verify that the LED status on the Arduino is lit up.
4. Press the increase button to verify the LED is receiving the “increase brightness” signal.
5. Press the decrease button to verify the LED is receiving the “decrease brightness” signal.
6. Ensure the LED is on
7. Use probe wires to verify frequency with oscilloscope

### 5.0 Measurable Criteria

The criteria for having a successful running prototype are as follows

### 5.2 T0 model:

I. The circuit board should be intact with the LED panel.
II. The LED should be at the front of the panel connected to the circuit board.
III. Upon plugging in the microcontroller and pressing down the button, the LED should start flashing.
IV. When toggling with the button, the LED should turn on and off within <1 second.

5

### 5.2 T9 model:

I. The circuit board should be intact with the LED panel.
II. | The LED should be facing the user when using the phone
III. | Upon plugging in the microcontroller and pressing the “Increase Brightness” button, the
| light should turn on and get brighter until it reaches maximum brightness.
IV. | When pressing the “Decrease Brightness” button, the LED brightness should dim until it is
| turned off.

### 6.0 Hardware Pinout

T0 model:

Pin Number | Usage/Description
3 | White LED Output
4 | LED ON/OFF Button Input

T9 model:

Pin Number | Usage/Description
0 | White LED Output
4 | Increase Brightness
3 | Decrease Brightness

6

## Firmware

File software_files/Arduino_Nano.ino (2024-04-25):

const int ledPin = 3; // Define the PWM capable pin connected to the LED
const int onButtonPin = 4; // Define the pin for the button to increase brightness
const unsigned long blinkInterval = 12.5; // 12.5 milliseconds (40Hz)
unsigned long previousMillis = 0; // Store the last time the LED state was changed
int brightness = 0; // Start withan  initial brightness of 128


// Debouncing variables
unsigned long lastDebounceTime = 0; // Stores the last time a button state change was detected
bool buttonState = HIGH; // Current state of the button
bool lastButtonState = HIGH; // Previous state of the button
const unsigned long debounceDelay = 50; // Debounce delay in milliseconds


void setup() {
  pinMode(ledPin, OUTPUT); // Set the LED pin as an OUTPUT
  pinMode(onButtonPin, INPUT_PULLUP); // Set the increase button pin as input with pull-up resistor
}

void loop() {
  unsigned long currentMillis = millis(); // Get the current time

  // Check if it's time to change the LED state
  previousMillis = currentMillis; // Save the last time the LED state was changed


  analogWrite(ledPin, brightness); // Set LED brightness
  delay(12.5); // Delay for 1/40 second
  analogWrite(ledPin, 0); // brightnessTurn off the LED
  delay(12.5); // Delay for another 1/40 second

  // Read the button input with debounce
  int reading = digitalRead(onButtonPin);

  // If the button state has changed, update the last debounce time
  if (reading != lastButtonState) {
    lastDebounceTime = currentMillis;
  }

  // If enough time has passed, consider the button state stable
  if ((currentMillis - lastDebounceTime) > debounceDelay) {
    // If the button state has changed, update the button state
    if (reading != buttonState) {
      buttonState = reading;

      // If the button is pressed (LOW), do something (e.g., increase brightness)
        // Check the increase button
      if (digitalRead(onButtonPin) == LOW) {
        // brightness = min(255, brightness + 5); // Increase brightness
        if (brightness == 0){
            brightness = 255;
            delay(100);
        }
        else {
          brightness = 0;
          delay(100);
        }
      }
      
    }
  }
  // Update the last button state
  lastButtonState = reading;
}

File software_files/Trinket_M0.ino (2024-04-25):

const int ledPin = 0; // Define the PWM capable pin connected to the LED
const int increaseButtonPin = 4; // Define the pin for the button to increase brightness
const int decreaseButtonPin = 3; // Define the pin for the button to decrease brightness
const unsigned long blinkInterval = 12.5; // 12.5 milliseconds (40Hz)
unsigned long previousMillis = 0; // Store the last time the LED state was changed
int brightness = 128; // Start withan  initial brightness of 128

void setup() {
  pinMode(ledPin, OUTPUT); // Set the LED pin as an OUTPUT
  pinMode(increaseButtonPin, INPUT_PULLUP); // Set the increase button pin as input with pull-up resistor
  pinMode(decreaseButtonPin, INPUT_PULLUP); // Set the decrease button pin as input with pull-up resistor
}

void loop() {
  unsigned long currentMillis = millis(); // Get the current time 

  // Check if it's time to change the LED state
  if (currentMillis - previousMillis >= blinkInterval) {
    previousMillis = currentMillis; // Save the last time the LED state was changed

    analogWrite(ledPin, brightness); // Set LED brightness
    delay(12.5); // Delay for 1/40 second
    analogWrite(ledPin, 0); // brightnessTurn off the LED
    delay(12.5); // Delay for another 1/40 second

    // Check the increase button
    if (digitalRead(increaseButtonPin) == LOW) {
      brightness = min(255, brightness + 5); // Increase brightness
    }

    // Check the decrease button
    if (digitalRead(decreaseButtonPin) == LOW) {
      brightness = max(0, brightness - 5); // Decrease brightness
    }
  }
}

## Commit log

2024-04-24 Rename T9 Model Circuit Diagram.png to T9_Model_Circuit_Diagram.png
2024-04-24 Rename t0 finished model circuit diagram.jpg to T0_Circuit_Diagram
2024-04-24 Rename t9 final model circuit diagram.jpg to T9_Circuit_Diagram.jpg
2024-04-24 moved files
    [T9_Trinket housing_cover.stl, T9_Trinket_housing.stl, T9_prototyping-board housing.stl]
2024-04-24 Rename T9_Trinket housing_cover.stl to T9_Trinket_housing_cover.stl
    [T9_Trinket_housing_cover.stl]
2024-04-24 Rename T9_prototyping-board housing.stl to T9_prototyping_board_housing.stl
    [T9_prototyping_board_housing.stl]
